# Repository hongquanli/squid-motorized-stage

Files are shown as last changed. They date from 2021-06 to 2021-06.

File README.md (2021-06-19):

# Squid motorized stages
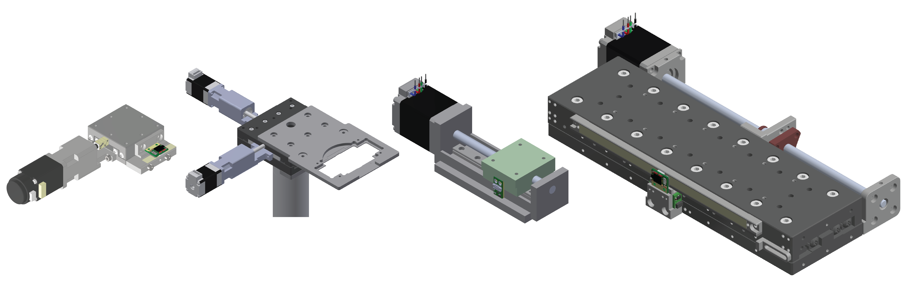
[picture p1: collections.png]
collections

## Stages
- [13 mm travel focus stage (ball bearing)](3%20mm%20travel%20fine%20adjustment%20ball%20bearing%20stage), with adapters for mounting Thorlabs SM1 lens tube
- [25 mm travel XY stage (ball bearing)](25%20mm%20travel%20XY%20ball%20bearing%20stage), with adapters for mounting glass slide or 35 mm glass bottom dish
- [50 mm travel XY stage (linear guideway with recirculating bell bearings)](50%20mm%20travel%20linear%20guideway%20stage%20for%20non-cantilevered%20load), used in gravitymachine
- [130 mm travel X or XY stage (cross roller bearing)](130%20mm%20travel%20cross%20roller%20bearing%20stage), with kinematic well plate holder. Also used for Nautilus (Octopi/Squid-based plate reader)

## Stage controller PCB


Right now we're using a custom PCB stack for controlling the stages. The microcontroller is an Arduino Due (we intend to switch to teensy 4.1) and the stepper motor drivers are Trinamic TMC2209 SilentStepSticks (we intend to switch to using Trinamic motion controller TMC4361 + one of the Trinamic stepper drivers so that the limit switches and encoders are interfaced by the motion controllers instead of the micontroller, which will also reduce the number of GPIOs needed from the micontroller). 

The driver stack development is led by Ethan (Github repo: [link](https://github.com/prakashlab/octopi-driver-board)). Currently used the PCB and PCBA fab files can be found on the squid-imaging website [www.squid-imaging.org](www.squid-imaging.org) and in [driver stack](driver%20stack).

## Control panel


BOM of the control panel can be found in [control panel](control%20panel)

## Software
The stages can be controled with the Arduino firmware and python software: 

Microscope software Github repo: [link](https://github.com/hongquanli/octopi-research), simple GUI example: [link](https://github.com/hongquanli/squid-tutorials/tree/main/example_stepper_control) (we also explained how the software is written in these two short READMEs: [overview](https://github.com/hongquanli/squid-tutorials/tree/main/example_led_control), [more detailed note](https://github.com/hongquanli/squid-tutorials/tree/main/example_led_control/software)).

## References
[1] Hongquan Li, Deepak Krishnamurthy, Ethan Li, Pranav Vyas, Nibha Akireddy, Chew Chai, Manu Prakash, "**Squid: Simplifying Quantitative Imaging Platform Development and Deployment**." BiorXiv [ [Github](https://github.com/hongquanli/octopi-research) | [preprint](https://doi.org/10.1101/2020.12.28.424613) | [website](https://squid-imaging.org)]

[2] Deepak Krishnamurthy, Hongquan Li, François Benoit du Rey, Pierre Cambournac, Adam G. Larson, Ethan Li, and Manu Prakash. "**Scale-free vertical tracking microscopy.**" Nature Methods 17, no. 10 (2020): 1040-1051. [ [Github](https://github.com/deepakkrishnamurthy/gravitymachine-research) | [paper](https://www.nature.com/articles/s41592-020-0924-7) | [website](https://gravitymachine.org) ]

[3] Janie R. Byrum, Eric Waltari, Owen Janson, Syuan-Ming Guo, Jenny Folkesson, Bryant B. Chhun, Joanna Vinden, Ivan E. Ivanov, Marcus L. Forst, Hongquan Li, Adam G. Larson, Wesley Wu1, Cristina M. Tato, Krista M. McCutcheon, Michael J. Peluso, Timothy J. Henrich, Steven G. Deeks, Manu Prakash, Bryan Greenhouse, John E. Pak, Shalin B. Mehta. "**multiSero: Open multiplex-ELISA platform for analyzing antibody responses to SARS-CoV-2 infection**." bioRxiv [ [preprint](https://doi.org/10.1101/2021.05.07.21249238) | [Github](https://github.com/czbiohub/pysero) ]

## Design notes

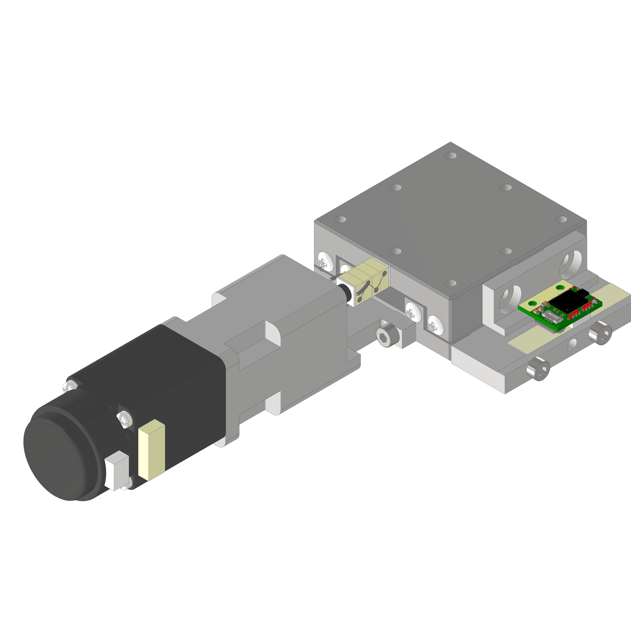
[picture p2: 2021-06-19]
13 mm travel fine adjustment ball bearing stage/CAD rendering.png

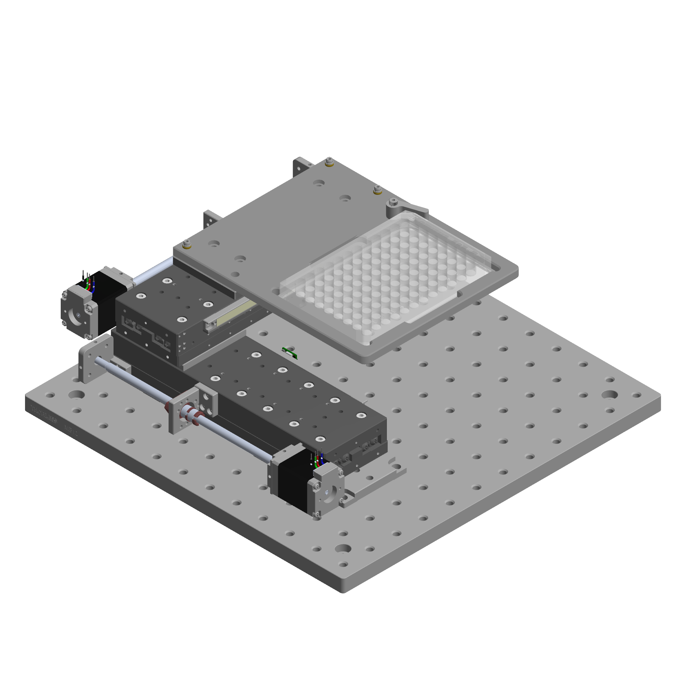
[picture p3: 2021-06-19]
130 mm travel cross roller bearing stage/motorized VRU3205 XY v2.0.png

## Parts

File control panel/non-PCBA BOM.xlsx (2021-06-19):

# | Description | Vendor | Part Number | Qty | Unit Price | Vendor Contact | Image Reference
 | Control Panel
1 | ~~analoy joystick (HE1, 2 Axis Low Profile Locked Z, 1 Button, Square Limiter, Rear Mount, 0-5v, Black)~~ | Ruffy Controls | ~~HE1-61-S-D-1-BK~~ | 1 | $135.00 | http://ruffycontrols.com/
 | analoy joystick (HE1, 2 Axis Low Profile Locked Z, 1 Button, Square Limiter, Rear Mount, 0-3.3v output, Black) | Ruffy Controls | HE1-61-S-D-3.3-BK | 1 | $135.00
2 | pre-crimped jumper for joystick | Digi-Key | H3BBG-10106-B4 | 6 | $0.77
3 | connector socket for joystick cable assembly | Digi-Key | DF11-12DS-2C | 2 | $0.25
4 | (PCBA) SMD header for joystick cable assembly | Digi-Key | DF11C-12DP-2V(57) | 1 | $2.11
5 | rotary encoder (magnetic) for focus adjustment | Digi-Key | EMS22Q31-B28-LS4 | 1 | $31.96
6 | knob for focus adjustment | Digi-Key | KLN1250B1/4 | 1 | $18.16
7 | cable assembly for rotary encoder | Digi-Key | A06KR06KR26E102B | 1 | $1.16
8 | (PCBA) SMD header for rotary encoder | Digi-Key | B6B-PH-SM4-TB(LF)(SN) | 1 | $0.77
9 | (PCBA) rotary potentiometer | Digi-Key | PCW1J-C24-BAB103L | 1 | $5.37
10 | knob for rotary potentiometer | Digi-Key | OEDA-63-4-5 | 2 | $7,74
11 | toggle switch with LED indicator | Digi-Key | M2112TFW02 | 1 | $11.96
12 | quick-connector contact for the toggle switch | Digi-Key | 61454-1 | 4 | $0.28
13 | (PCBA) SMD header for toggle switch | Digi-Key | 1778719 | 1 | $1.28
14 | plug for toggle switch | Digi-Key | 1704857 | 1 | $1.42
15 | ~~(PCBA) 12 pin picolock SMD header for driver stack connection~~ | ~~Digi-Key~~ | ~~5040501291~~ | ~~1~~ | ~~$1.76~~
16 | ~~(PCBA) 4 pin picolock SMD header for driver stack connection~~ | ~~Digi-Key~~ | ~~5040500491~~ | ~~1~~ | ~~$0.85~~
 | (PCBA) 8 pin picolock SMD header for driver stack connection | Digi-Key | 5040500891 | 1
 | (PCBA) 6 pin picolock SMD header for driver stack connection | Digi-Key | 5040500691 | 1
17 | ~~12 pin picklock cable assembly ~~ | ~~Digi-Key~~ | ~~151321206~~ | ~~1~~ | ~~$7.28~~
18 | ~~4 pin picklock cable assembly ~~ | ~~Digi-Key~~ | ~~151320406~~ | ~~1~~ | ~~$3.64~~
 | 8 pin picklock cable assembly | Digi-Key | 151320806
 | 6 pin picklock cable assembly | Digi-Key | 151320606
22 | ~~5V step-up~~ | Pololu | ~~2564~~ | 1 | $4.49
23 | aluminum enclosure | polycase | al-77p | 1 | $14.26
24 | thread-forming screws for the case | McMaster-Carr | 93878A148 | 6
Total: $363.94

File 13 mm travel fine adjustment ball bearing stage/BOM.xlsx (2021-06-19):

# | Description | Vendor | Part Number / File for CNC machining | Qty | Unit Price | Vendor Contact | Image Reference
 | Motorized Focus Assembly
1 | ball bearing linear stage, stainless steel, ±6.5mm | dg-sl (http://www.dg-sl.com/) | LBX40-C (product page) (http://www.dg-sl.com/plus/view.php?aid=367) | 1 | $61.14 | https://seln.taobao.com
2 | adapter for mounting SM1TC to LBX40-C | XTJ-tech | adapter_LBX40_SM1TC(thick)_v2.zip (https://drive.google.com/file/d/1vSxkDf_U7Hy0DEYcMtg9wJZE37Ds1pc6/view?usp=sharing) | 1 | $25.00 | katie@xtj-tech.com
3 | adapter for mounting LBX40-C to C1511 | XTJ-tech | adapter_LBX40_C1511_v3.zip (https://drive.google.com/file/d/1vVJ2LQsEshlLTpUiCyFs6SZvvZQxfeaH/view?usp=sharing) | 1 | $25.00
4 | adapter for mounting 21H4U to LBX40-C | XTJ-tech | adapter_LBX40_21H4U_v3.stp (https://drive.google.com/file/d/1vdc5DMPaTfWaKH6Y-Y7UMupx3H2Tfn9w/view?usp=sharingg) | 1 | $55.00
5 | size 8 captive linear actuator, 6e-5 in/step | Haydon kerk | 21H4U-2.5-A98 v1 (based on 21H4U-2.5-907) (https://prototypes.haydonkerk.com/ecatalog/hybrid-linear-actuators/en/linear-actuator-21H4U-2.5-907) | 1 | $130.45
6 | optional piezo stack actuator, 11.2 um travel (no load) | Thorlabs | PK2FMP2 | 0 | $62.25
 | optional amplified piezo actuator, 220 um travel (no load) | Thorlasb | PK2FSF1 | 0 | $366.83
 | optional amplified piezo actuator, 420 um travel (no load) | Thorlasb | PK2FVF1 | 0 | $480.46
7 | Clamp for SM1 Lens Tubes | Thorlabs | SM1TC | 1 | $45.72
8 | SM1 Lens Tube, 0.3" threaded depth | Thorlabs | SM1L03 | 1 | $12.52
9 | SM1 adapter for Objectives with RMS thread (Olympus, BoliOptics) | Thorlabs | SM1A3 | 1 | $18.50
10 | SM1 adapter for Nikon Objectives | Thorlabs | SM1A12 | 0 | $21.86
11 | M3 x 15 mm (or 14 mm) socket head screws for mounting the top plate for LBX40-C (line 2) [11.5 mm + 3.5 mm/5mm] | McMaster-Carr | 91292A346 or 91292A027 | 4
12 | M3 x 5 mm socket head screws for mounting the LBX40-C assembly to the adapter plate for C1511 | McMaster-Carr | 91292A110 | 4
13 | 8-32 x 1/2" socket head screws for mounting the assembly to C1511 | McMaster-Carr | 92196A194 | 4
14 | 8-32 x 1/4" socket head screws for mounting SM1TC | McMaster-Carr | 92196A190 | 1
15 | M2.5 x 8 mm socket head screws for adapter mounting linear actuator assembly to LBX40-C | McMaster-Carr | 91292A012 | 2
16 | M2 x 6 mm socket head screws for mounting the linear actuator |  |  | 4
Total: $312.19
 | Motorized Focus Assembly Optical Encoder Addon (optional)
1 | Optira Incremental, 5V Input, 5nm Resolution | Celera Motion | PIA-0005-A1-05-A | 1 | RFQ (we're asked by the vendor to not disclose the price) | https://www.celeramotion.com/request-a-quote/
2 | Optira Tape Scale, 20um w/Center Index, 30mm Long | Celera Motion | 124-40030-B-I | 1 | RFQ (we're asked by the vendor to not disclose the price) | https://www.celeramotion.com/request-a-quote/
3 | adapter for mouting the optira PI encoder to LBX40-C | XTJ-tech | adapter_LBX40_Optira PI.zip (https://drive.google.com/file/d/1vdktcWQU654wsF2iJLESckWOvEwZ94rC/view?usp=sharing) | 1 | $15.00
4 | adapter for mouting the optira tape to LBX40-C | XTJ-tech | adapter_LBX40_Optira PI tape 30mm.stp (https://drive.google.com/file/d/1vjwUcNyPCBcBCZTBB1smuDJui9zGkcLM/view?usp=sharing) | 1 | $15.00
5 | M1.6 x 2 mm socket head screw for mounting the encoder | McMaster-Carr | 92290A847 (or 92000A040) | 2
6 | M3 x 3 mm low profile socket head screw for mounting the encoder adapter to LBX40-C | McMaster-Carr | 90666A100 | 2
7 | M2.5 x 18 mm socket head screw for mounting the tape adapter to LBX40-C | McMaster-Carr | 91292A028 | 2
(Total: <$400)
 | Cage Cube Addon for Epifluorescence/Patterned Illumination/Active Drift Correction/3D Focus Tracking etc. (optional)
1 | mounting adapter for CM1-DCH | XTJ-tech | adapter_CM1-DCH_v2.zip (https://drive.google.com/file/d/1vmlo_wTWzoKCbnt8HrBpzqPNQ9Hj7mCo/view?usp=sharing) | 1 | $30.00
2 | Cage Cube for Rectangular Optics | Thorlabs | CM1-DCH | 1 | $175.31
3 | Cage Cube Connector for additional CM1-DCH | Thorlabs | CM1-CC | 0 | $48.70
4 | additional cage cubes | Thorlabs | CM1-DCH | 0 | $175.31
5 | Externally SM1-Threaded End Cap | Thorlabs | SM1CP2 | 2 | $18.83
6 | 8-32 socket head screw for mounting the CM1-DCH adapter | McMaster-Carr | 92196A190 | 4
7 | 2 mm dia. x 5 mm length Dowel pin | McMaster-Carr | 91585A189 | 2
(Total: $205.31)

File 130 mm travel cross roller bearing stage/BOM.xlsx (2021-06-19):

# | Description | Vendor | Part Number / File for CNC machining | Qty | Unit Price | Vendor Contact | Image Reference
 | 130 mm travel motorized cross roller stage - single axis, bare minimum
 | SELN VRU3-205 stage, modified | dg-sl (http://www.dg-sl.com/) | SELN-VRU3-205-02 (based on http://www.dg-sl.com/plus/view.php?aid=143) | 1 | $100.00
 | PBC linear motorized lead screw | PBCLinear | https://theconfig.com/07895591C3 | 1 | $162.40
 | VRU3 motor mount | XTJ-tech | see custom machined parts folder | 1 | $20.00
 | VRU3 nut mount | XTJ-tech | see custom machined parts folder | 1 | $15.00
 | VRU3 bearing mount | XTJ-tech | see custom machined parts folder | 1 | $20.00
 | iglide® L280, sleeve bearing for fast rotating applications | Igus | https://www.igus.com/product/7?artNr=LSM-0507-05 | 1 | $1.45
 | Total: $318.85
 | XY stage with kinematic mounted plate holder
 | SELN VRU3-205 stage, modified | dg-sl (http://www.dg-sl.com/) | see custom machined parts folder | 2 | $100.00
 | PBC linear motorized lead screw | PBCLinear | https://theconfig.com/07895591C3 | 2 | $162.40
 | VRU3 motor mount | XTJ-tech | see custom machined parts folder | 2 | $20.00
 | VRU3 nut mount | XTJ-tech | see custom machined parts folder | 2 | $15.00
 | VRU3 bearing mount | XTJ-tech | see custom machined parts folder | 2 | $20.00
 | iglide® L280, sleeve bearing for fast rotating applications | Igus | https://www.igus.com/product/7?artNr=LSM-0507-05 | 1 | $1.45
 | limit switch magnet mount | XTJ-tech | see custom machined parts folder | 4 | $10.00
 | limit switch mount | XTJ-tech | see custom machined parts folder | 2 | $20.00
 | VRU3 base | XTJ-tech | see custom machined parts folder | 2 | $25.00
 | XY adapting plate | XTJ-tech | see custom machined parts folder | 1 | $15.00
 | well plate holder (MIC-6 Al) | XTJ-tech | see custom machined parts folder | 1 | $50.00
 | well plate holder base | XTJ-tech | see custom machined parts folder | 1 | $25.00
 | well plate clamp | XTJ-tech | see custom machined parts folder | 1 | $10.00
 | custom torsion spring | XTJ-tech | see custom machined parts folder | 1 | $1.50
 | sapphire contact pad | Thorlabs | https://www.thorlabs.com/thorproduct.cfm?partnumber=P25SK2 | 1 | $7.09
 | Threaded Bushing | Thorlabs | https://www.thorlabs.com/thorproduct.cfm?partnumber=N100B2P | 3 | $4.96
 | F19SS050 Adjusters | Thorlabs | https://www.thorlabs.com/thorproduct.cfm?partnumber=F19SS050 | 3 | $4.69
 | Locking Collar | Thorlabs | https://www.thorlabs.com/thorproduct.cfm?partnumber=F19SC1 | 3 | $5.51
 | Total: $920.32
 | Optional or magnetic linear encoders and scales
 | RLC2IC magnetic increamental encoder + scale, 0.244 um resolution | RLS | https://www.rls.si/eng/rlc2ic-miniature-linear-and-rotary-pcb-level-incremental-magnetic-encoder?partNumbers=RLC2ICA13BB00A00%2CMS05BM156AM078 | 1 | $103.10
 | Optira™ Series – PI optical encoder, down to 5 nm resolution | Celera Motion | https://www.celeramotion.com/microe/products/linear-encoders/nano/optira-series-pi/ | 1 | RFQ
 | MS 15 optical encoder, down to 50 nm resolution | RSF | https://www.rsf.at/en/products/length-measurement/exposed-models/ms15/ | 1 | RFQ

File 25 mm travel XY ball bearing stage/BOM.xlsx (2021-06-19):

# | Description | Vendor | Part Number / File for CNC machining | Qty | Unit Price | Vendor Contact | Image Reference
 | 30 mm x 30 mm travel motorized stage (the specified travel of the stage is 25 mm but actual travel is larger - close to 30 mm x 30 mm)
1 | cross roller bearing linear stage, aluminum, ±12.5mm | dg-sl (http://www.dg-sl.com/) | LY80-CB (product page) (http://www.dg-sl.com/plus/view.php?aid=430) | 1 | $168.00 | https://seln.taobao.com
2 | size 8 captive linear actuator | Nanotec | LGA201S06-B-TDBA-038 | 2 | $152.00 | https://us.nanotec.com/products/2838-lga201s06-b-tdba-038
3 | adapter for mounting linear actuator to LY80-CB | XTJ-tech | adapter_LY80-CB_LGA20.stp (https://drive.google.com/file/d/1vr1I-hMQn7dr2koNRlnyY5aXdwgQq6TP/view?usp=sharing) | 2 | $25.00
4 | adapter for mounting LY80-CB to 1.5" post | XTJ-tech | adapter_LY80-CB_post_v2.zip (https://drive.google.com/file/d/1vok4e4640o_f0QpNSyhCTgKP9MVfUR3V/view?usp=sharing) | 1 | $20.00
5 | glass slide/petridish holder (MIC-6 Al) | XTJ-tech | sample holder_v2.1.stp (https://drive.google.com/file/d/1voHS16IwZe9Dwx52aForPZ1XCP-zlX9y/view?usp=sharing) | 1 | $35.00
6 | M4 x 10 mm socket head screw | McMaster-Carr | 91292A116 | 4
7 | 1/4-20 set screw |  |  | 1
8 | M4 low profile socket head screw (4 mm length) | McMaster-Carr | 92855A401 | 4
Total: $577.00

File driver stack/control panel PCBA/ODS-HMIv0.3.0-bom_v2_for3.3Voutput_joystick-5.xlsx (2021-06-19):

ODS-HMIv0.3.0-bom-2
Designator | Quantity | Supplier Link | Component Name | Manufacturer | Manufacturer Part # | Footprint | Supplier | Supplier Part # | Supplier Description | Mounting Type | Notes
J1 | 1 | https://www.digikey.com/en/products/detail/molex/5040500891/4693487 | 1x8 1.5mm Pitch Right-Angle Header | Molex | 5040500891 | 1x8POS | Digi-Key | WM14421CT-ND | CONN HEADER SMD R/A 8POS 1.5MM | SMT
J2 | 1 | https://www.digikey.com/en/products/detail/5040500691/WM10143CT-ND/4357143 | 1x6 1.5mm Pitch Right-Angle Header | Molex | 5040500691 | 1x6POS | Digi-Key | WM10143CT-ND | CONN HEADER SMD R/A 6POS 1.5MM | SMT
J3 | 1 | https://www.digikey.com/en/products/detail/jst-sales-america-inc/B6B-PH-SM4-TBT-LF-SN/9918862 | JST 1x6 Right-Angle Shrouded PH Header | JST | B6B-PH-SM4-TBT(LF)(SN) | 1x6POS | Digi-Key | 455-3363-1-ND | CONN HEADER SMD 6POS 2MM | SMT
U1,U2 | 2 | https://www.digikey.com/en/products/detail/bourns-inc/PCW1J-C24-BAB103L/3534177 | Rotary Potentiometer | Bourns | PCW1J-C24-BAB103L | 1x3POS | Digi-Key | PCW1J-C24-BAB103L-ND | POT 10K OHM 3/4W PLASTIC LINEAR | PTH
J4,J5 | 2 | https://www.digikey.com/en/products/detail/phoenix-contact/1778719/5131543 | Phoenix 1x4 Shrouded SSL Header | Phoenix Contact | 1778719 | 1x4POS | Digi-Key | 277-10160-1-ND | HEADER 4POS SMT WHITE | SMT
CN1 | 1 | https://www.digikey.com/en/products/detail/hirose-electric-co-ltd/DF11C-12DP-2V-57/4282018 | Hirose 2x6 Shrouded DF11 Header | Hirose | DF11C-12DP-2V(57) | 2x6POS | Digi-Key | H124541CT-ND | CONN HEADER SMD 12POS 2MM | SMT
R1 | 1 | https://www.digikey.com/en/products/detail/yageo/RC0805FR-0749R9L/727984 | 49.9 0805 resistor | Yageo | RC0805FR-0749R9L | 805 | Digi-Key | 311-49.9CRTR-ND | RES SMD 49.9 OHM 1% 1/8W 0805 | SMT
R3,R5 | 3 | https://www.digikey.com/en/products/detail/yageo/RC0805FR-0710KL/727535 | 0ohm 0805 resistor | Yageo | RC0805FR-0710KL | 805 | Digi-Key | 311-10.0KCRTR-ND | RES SMD 10K OHM 1% 1/8W 0805 | SMT
R2 | 3 | https://www.digikey.com/en/products/detail/yageo/RC0805FR-0710KL/727535 | 10K 0805 resistor | Yageo | RC0805FR-0710KL | 805 | Digi-Key | 311-10.0KCRTR-ND | RES SMD 10K OHM 1% 1/8W 0805 | SMT
R4,R6 | 2 | https://www.digikey.com/en/products/detail/yageo/RC0805FR-0720KL/727720 | DNI | Yageo | RC0805FR-0720KL | 805 | Digi-Key | 311-20.00KCRCT-ND | RES SMD 20K OHM 1% 1/8W 0805 | SMT
R7 | 1 | https://www.digikey.com/en/products/detail/yageo/RC0805FR-07499RL/727986 | 499 0805 resistor | Yageo | RC0805FR-07499RL | 805 | Digi-Key | 311-499CRTR-ND | RES SMD 499 OHM 1% 1/8W 0805 | SMT

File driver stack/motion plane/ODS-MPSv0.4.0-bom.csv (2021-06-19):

Designator | Quantity | Supplier Link | BOM ID | Component ID | Image | Component Name | Manufacturer | Manufacturer Part # | Footprint | Supplier | Supplier Part # | Supplier Description | Mounting Type | Notes
H1,H3,H2 | 3 | https://www.pololu.com/product/2749 | 2 | 5 |  | 2x20 Female Header, Tall Stacking | Sullins Connector Solutions | PPPC202LFHN-M53 RC | 2x20POS | Pololu | 2749 | Stackable 0.100″ Female Header with Extra 0.3″ Spacer: 2x20-Pin, Straight | PTH | The female side should be on the underside of the board, while the male pins should stick up.
H4, H5, H6, H7, H8, H9, H10, H11 | 8 | https://www.digikey.com/product-detail/en/sullins-connector-solutions/NPPC081KFXC-RC/S5639-ND/776098 | 4 | 17 |  | 1x8 Female SMT Header | Sullins Connector Solutions | NPPC081KFXC-RC | 1x8POS | Digi-Key | S5639-ND | CONN HDR 8POS 0.1 GOLD SMD | SMT
C1,C2,C3,C4 | 4 | https://www.digikey.com/product-detail/en/nichicon/UCD1E470MCL1GS/493-6385-1-ND/3438899 | 6 | 18 |  | 47uF Electrolytic Capacitor | Nichicon | UCD1E470MCL1GS | 6.6mmx6.6mm | Digi-Key | 493-6385-1-ND | CAP ALUM 47UF 20% 25V SMD | SMT
J5 | 1 | https://www.digikey.com/product-detail/en/cui-devices/PJ-037AH-SMT-TR/CP-037AHPJCT-ND/1530998 | 7 | 19 |  | DC Power Jack | CUI Devices | PJ-037AH-SMT-TR | SMT | Digi-Key | CP-037AHPJCT-ND | CONN PWR JACK 2X5.5MM SOLDER | SMT
LED1,LED2 | 2 | https://www.digikey.com/product-detail/en/everlight-electronics-co-ltd/17-21SYGC-S530-E2-TR8/1080-1500-1-ND/7707772 | 8 | 20 |  | Green Indicator LED | Everlight Electronics | 17-21SYGC/S530-E2/TR8 | 805 | Digi-Key | 1080-1500-1-ND | LED YELLOW/GREEN CLEAR 0805 SMD | SMT
R1,R3 | 2 | https://www.digikey.com/product-detail/en/%E5%9E%88-%C3%A1/RC1206FR-071KL/311-1-00KFRCT-ND/731334 | 9 | 21 |  | 1K 1206 Resistor | Yageo | RC1206FR-071KL | 1206 | Digi-Key | 311-1.00KFRCT-ND | RES SMD 1K OHM 1% 1/4W 1206 | SMT
R2 | 1 | https://www.digikey.com/product-detail/en/%E5%9E%88-%C3%A1/RC1206FR-07100RL/311-100FRCT-ND/731438 | 10 | 22 |  | 100 1206 Resistor | Yageo | RC1206FR-07100RL | 1206 | Digi-Key | 311-100FRCT-ND | RES SMD 100 OHM 1% 1/4W 1206 | SMT
J1,J2,J3,J4 | 4 | https://www.digikey.com/product-detail/en/phoenix-contact/1814935/277-9965-1-ND/4696094 | 11 | 30 |  | 1x4 Feed-Through Header | Phoenix Contact | 1814935 | 1x4POS | Digi-Key | 277-9965-1-ND | CONN HEADER 4POS 2.5MM SMD | SMT
J7,J8,J9,J10 | 4 | https://www.digikey.com/product-detail/en/jst-sales-america-inc/S6B-ZR-SM4A-TF-LF-SN/455-1610-1-ND/858041 | 12 | 25 |  | 1x6 1.5mm Pitch Right-Angle Header | JST | S6B-ZR-SM4A-TF(LF)(SN) | 1x6POS | Digi-Key | 455-1610-1-ND | CONN HEADER SMD R/A 6POS 1.5MM | SMT
J11 | 1 | https://www.digikey.com/product-detail/en/molex/0022292041/WM2746-ND/1130590 | 13 | 26 |  | 1x4 KK 254 Male Header | Molex | 22292041 | 1x4POS | Digi-Key | WM2746-ND | CONN HEADER VERT 4POS 2.54MM | PTH | Solder so that the plastic tab is closer to the outer perimeter of the board.
U2,U3 | 2 | https://www.digikey.com/product-detail/en/nexperia-usa-inc/74LVC07AD-118/1727-3089-1-ND/946746 | 14 | 27 |  | 6-Bit Buffer | Nexperia | 74LVC07AD,118 | 14-SOIC | Digi-Key | 1727-3089-1-ND | IC BUFFER NON-INVERT 5.5V 14SO | SMT
J12 | 1 | https://www.digikey.com/en/products/detail/molex/5040500891/4693487 | 15 | 44 |  | 1x8 1.5mm Pitch Right-Angle Header | Molex | 5040500891 | 1x8POS | Digi-Key | WM14421CT-ND | CONN HEADER SMD R/A 8POS 1.5MM | SMT | On the underside of the board.
J13 | 1 | https://www.digikey.com/en/products/detail/5040500691/WM10143CT-ND/4357143 | 16 | 45 |  | 1x6 1.5mm Pitch Right-Angle Header | Molex | 5040500691 | 1x6POS | Digi-Key | WM10143CT-ND | CONN HEADER SMD R/A 6POS 1.5MM | SMT | On the underside of the board.
R4,R5,R6,R7,R8,R9,R10,R11,R12,R13,R14,R15 | 12 | https://www.digikey.com/en/products/detail/yageo/RC0805FR-074K7L/727929 | 17 | 33 |  | 4.7K 0805 Resistor | Yageo | RC0805FR-074K7L | 805 | Digi-Key | 311-4.70KCRCT-ND | RES SMD 4.7K OHM 1% 1/8W 0805 | SMT | On the underside of the board.

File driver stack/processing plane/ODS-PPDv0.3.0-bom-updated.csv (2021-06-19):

Designator | Comment | Quantity | Supplier Link | Component Name | Manufacturer | Manufacturer Part # | In OPL? | Footprint | Supplier | Supplier Part # | Supplier Description | Mounting Type | Notes
H1,H3,H2 |  | 3 | https://www.pololu.com/product/2749 | 2x20 Female Header, Tall Stacking | Sullins Connector Solutions | PPPC202LFHN-M53 RC | Yes | 2x20POS | Pololu | 2749 | Stackable 0.100″ Female Header with Extra 0.3″ Spacer: 2x20-Pin, Straight | PTH | Alternative: PRT-16763 (SparkFun or DigiKey)
SPI |  | 1 | https://www.pololu.com/product/1023 | 2x3 Female PTH Header | Pololu | 1023 | Yes | 2x3POS | Pololu | 1023 | 0.100" (2.54 mm) Female Header: 2x3-Pin, Straight | PTH
DUE1 | Note for ordering: do not order separately, break 1x40 header (see last line) | 1 | https://www.pololu.com/product/965 | 1X10 Male PTH Header | Pololu | 965 | Yes | 1x10POS | Pololu | 965 | 0.100" (2.54 mm) Breakaway Male Header: 1×40-Pin, Straight, Black | PTH
DUE2, DUE3, DUE5, DUE6, DUE7 | Note for ordering: do not order separately, break 1x40 header (see last line) | 5 | https://www.pololu.com/product/965 | 1X8 Male PTH Header | Pololu | 965 | Yes | 1x8POS | Pololu | 965 | 0.100" (2.54 mm) Breakaway Male Header: 1×40-Pin, Straight, Black | PTH
DUE4 | Note for ordering: do not order separately, break 1x40 header (see last line) | 1 | https://www.pololu.com/product/966 | 2x18 Male PTH Header | Pololu | 966 | Yes | 2x18POS | Pololu | 966 | 0.100" (2.54 mm) Breakaway Male Header: 2×40-Pin, Straight | PTH
J1 |  | 1 | https://www.digikey.com/en/products/detail/molex/5040500891/4693487 | 1x8 1.5mm Pitch Right-Angle Header | Molex | 5040500891 | Yes | 1x12POS | Digi-Key | WM14421CT-ND | CONN HEADER SMD R/A 8POS 1.5MM | SMT
J2,J6 |  | 2 | https://www.digikey.com/en/products/detail/5040500691/WM10143CT-ND/4357143 | 1x6 1.5mm Pitch Right-Angle Header | Molex | 5040500691 | Yes | 1x4POS | Digi-Key | WM10143CT-ND | CONN HEADER SMD R/A 6POS 1.5MM | SMT
J7,J8,J9,J10 |  | 4 | https://www.digikey.com/en/products/detail/phoenix-contact/1814663/4452958 | 1x5 Spring Clamp Terminal Block | Phoenix Contact | 1814663 | Yes | 1x5POS | Digi-Key | 277-10065-1-ND | TERM BLOCK 5POS | SMT
U1,U2 |  | 2 | https://www.digikey.com/en/products/detail/texas-instruments/SN74LV1T34DBVR/4555575 | SOT-23 Non-Inverting Buffer | Texas Instruments | SN74LV1T34DBVR | Yes | SOT-23-5 | Digi-Key | 296-37176-1-ND | IC BUF NON-INVERT 5.5V SOT23-5 | SMT
R1,R2 |  | 2 | https://www.digikey.com/en/products/detail/yageo/RC0603JR-0768RL/726821 | 68 Ohm 0603 Resistor | Yageo | RC0603JR-0768RL | Yes | 603 | Digi-Key | 311-68GRCT-ND | RES SMD 68 OHM 5% 1/10W 0603 | SMT
2.54 mm header | Part for DUE1-DUE7 | 3 | https://www.pololu.com/product/965

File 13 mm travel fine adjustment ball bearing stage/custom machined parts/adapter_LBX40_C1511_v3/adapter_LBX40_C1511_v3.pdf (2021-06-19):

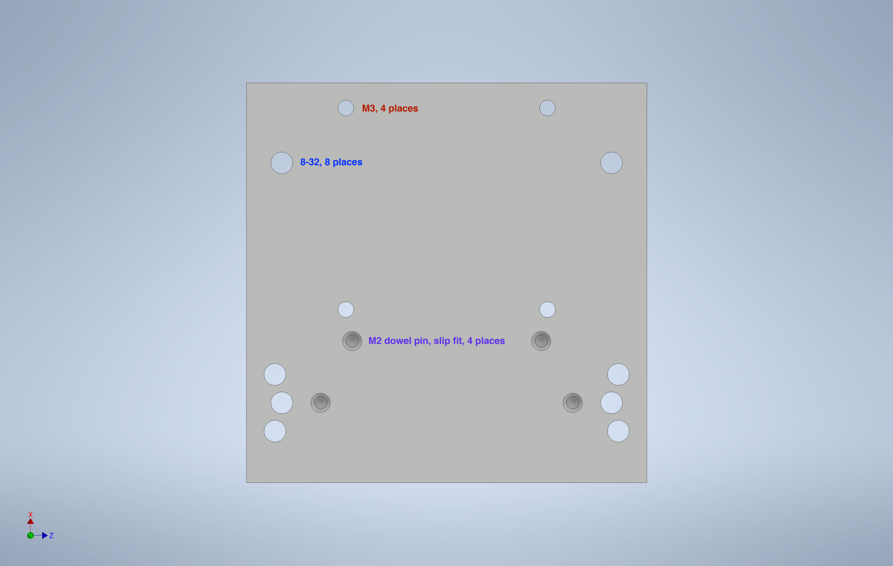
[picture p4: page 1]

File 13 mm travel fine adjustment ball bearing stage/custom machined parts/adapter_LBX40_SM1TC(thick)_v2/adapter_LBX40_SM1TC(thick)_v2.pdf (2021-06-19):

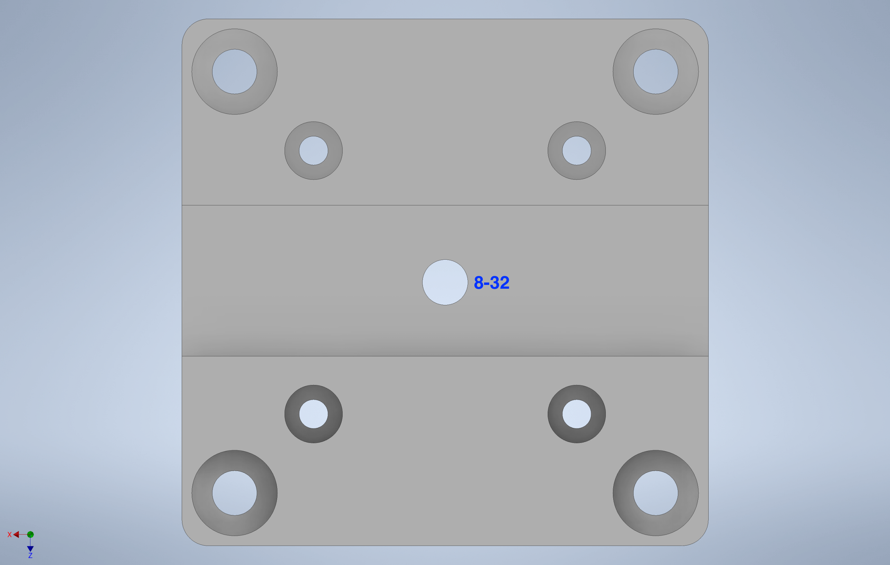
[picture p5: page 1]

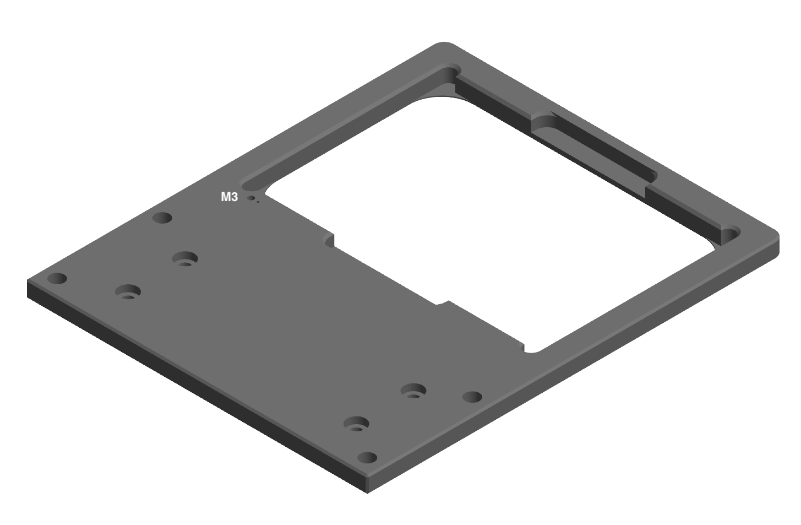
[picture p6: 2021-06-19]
130 mm travel cross roller bearing stage/custom machined parts/clamping well plate holder_20210318.png

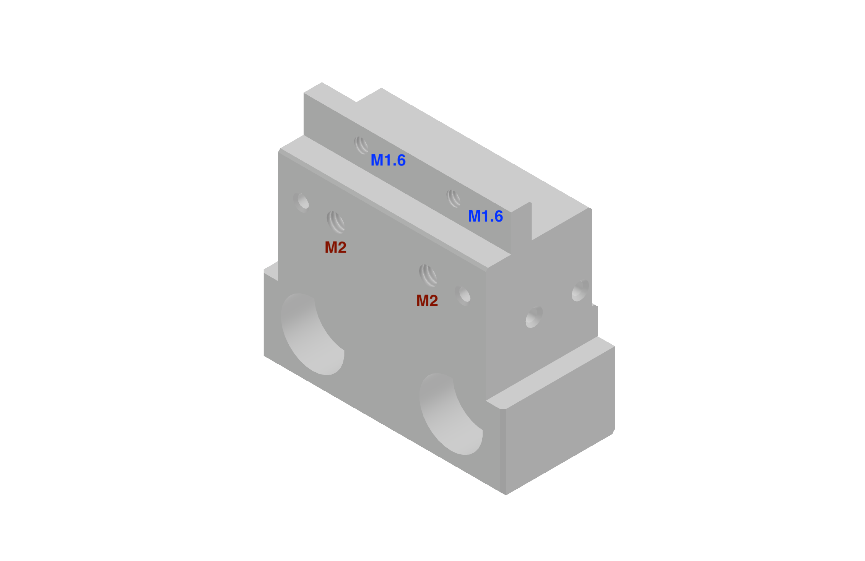
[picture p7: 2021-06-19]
130 mm travel cross roller bearing stage/custom machined parts/optira encoder mounting adapter - VRU3_20210324.png

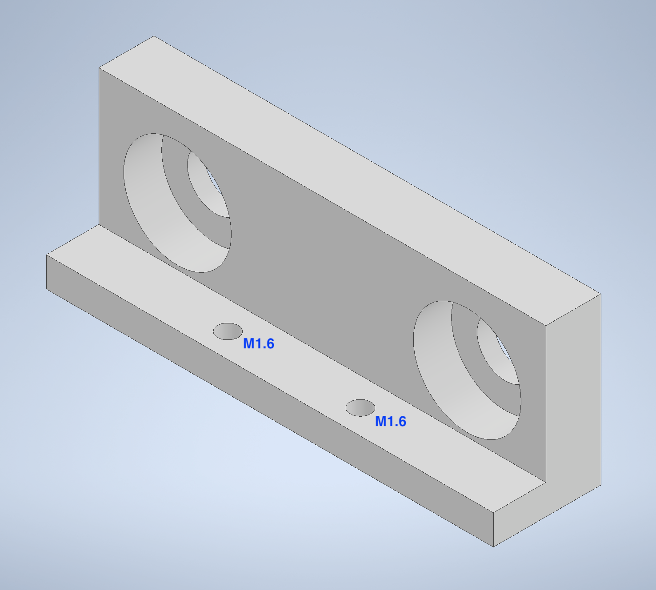
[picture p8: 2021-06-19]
13 mm travel fine adjustment ball bearing stage/custom machined parts/adapter_LBX40_Optira PI/adapter_LBX40_Optira PI.png

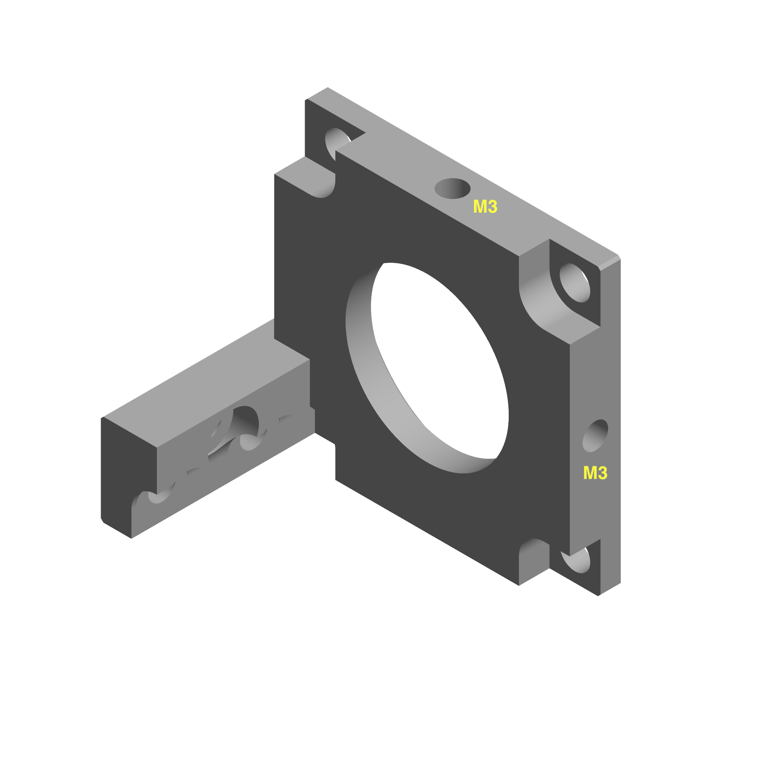
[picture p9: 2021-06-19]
130 mm travel cross roller bearing stage/custom machined parts/VRU-NEMA11 motor mount - direct attachment v2_20210325.png

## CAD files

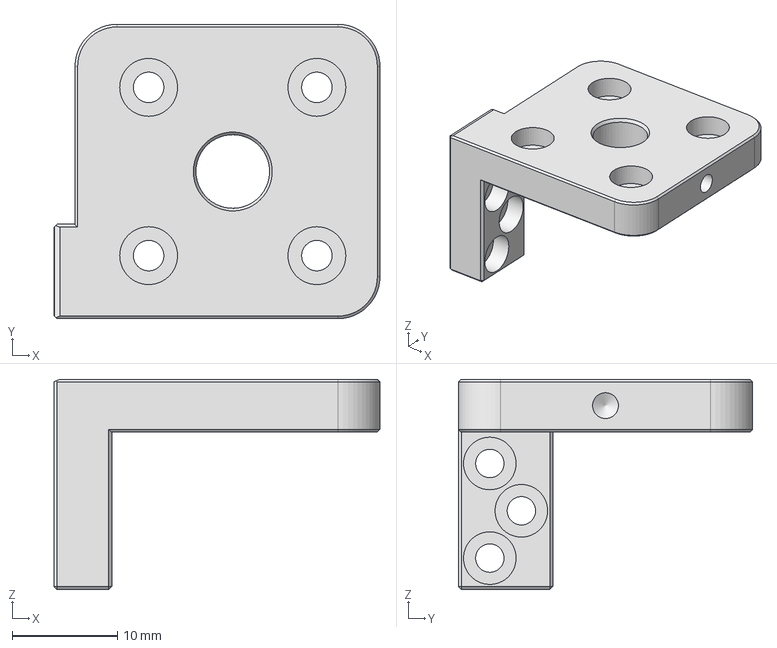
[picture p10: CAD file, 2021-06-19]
130 mm travel cross roller bearing stage/custom machined parts/VRU-NEMA11 motor mount bearing support - fullsize_20210325.stp
31.0 x 28.0 x 20.0 mm

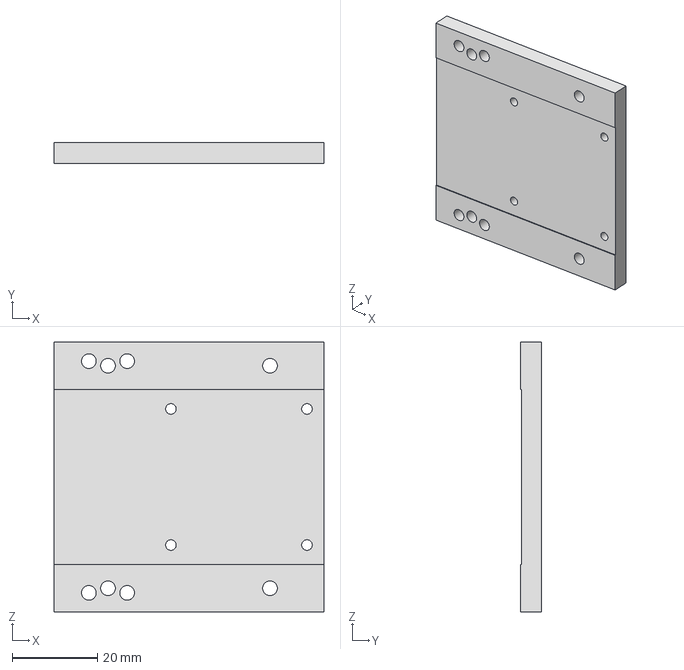
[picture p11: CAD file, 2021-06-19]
13 mm travel fine adjustment ball bearing stage/custom machined parts/adapter_LBX40_C1511_v3/adapter_LBX40_C1511_v3.stp
63.5 x 5.00 x 63.5 mm

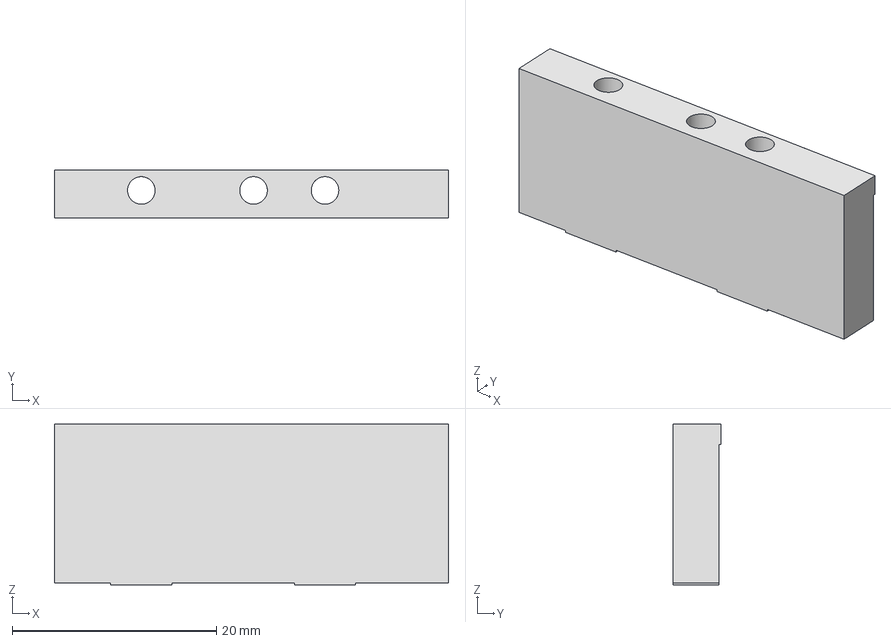
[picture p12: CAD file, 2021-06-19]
13 mm travel fine adjustment ball bearing stage/custom machined parts/adapter_LBX40_Optira PI tape 30mm.stp
38.6 x 4.70 x 15.7 mm

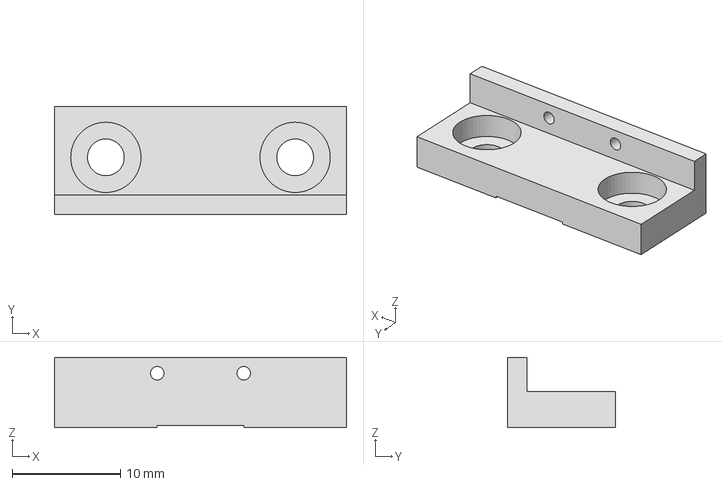
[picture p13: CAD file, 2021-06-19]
13 mm travel fine adjustment ball bearing stage/custom machined parts/adapter_LBX40_Optira PI/adapter_LBX40_Optira PI.stp
27.0 x 10.0 x 6.50 mm

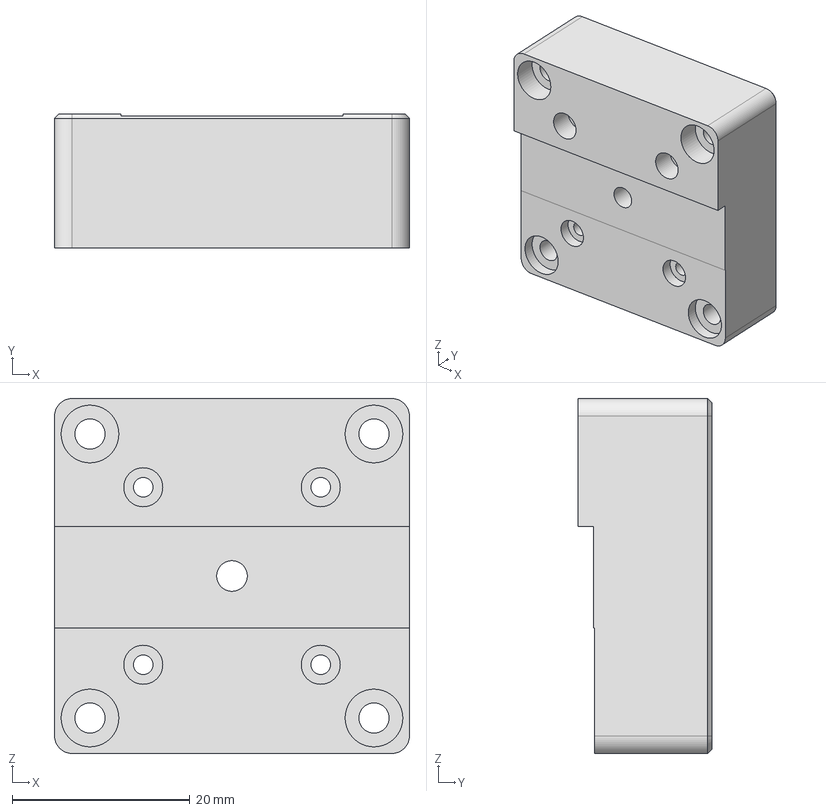
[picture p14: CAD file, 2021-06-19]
13 mm travel fine adjustment ball bearing stage/custom machined parts/adapter_LBX40_SM1TC(thick)_v2/adapter_LBX40_SM1TC(thick)_v2.stp
40.0 x 15.1 x 40.0 mm

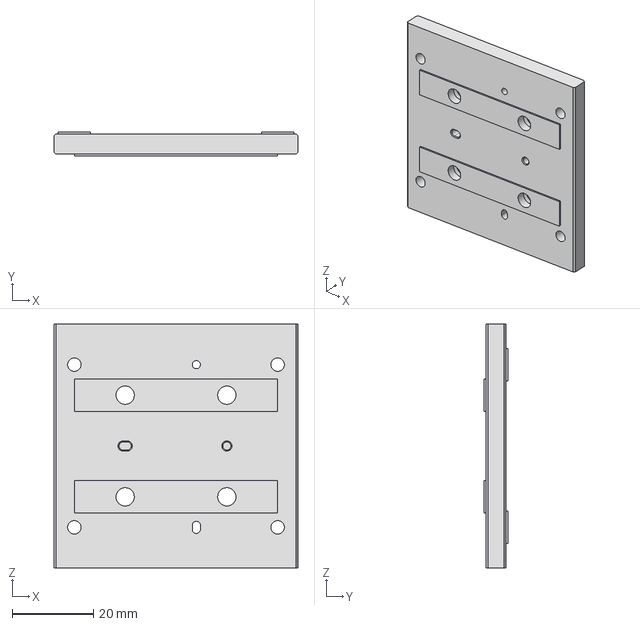
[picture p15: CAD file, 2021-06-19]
130 mm travel cross roller bearing stage/custom machined parts/VRU3 XY adapter_20210106.stp
60.0 x 6.00 x 60.0 mm

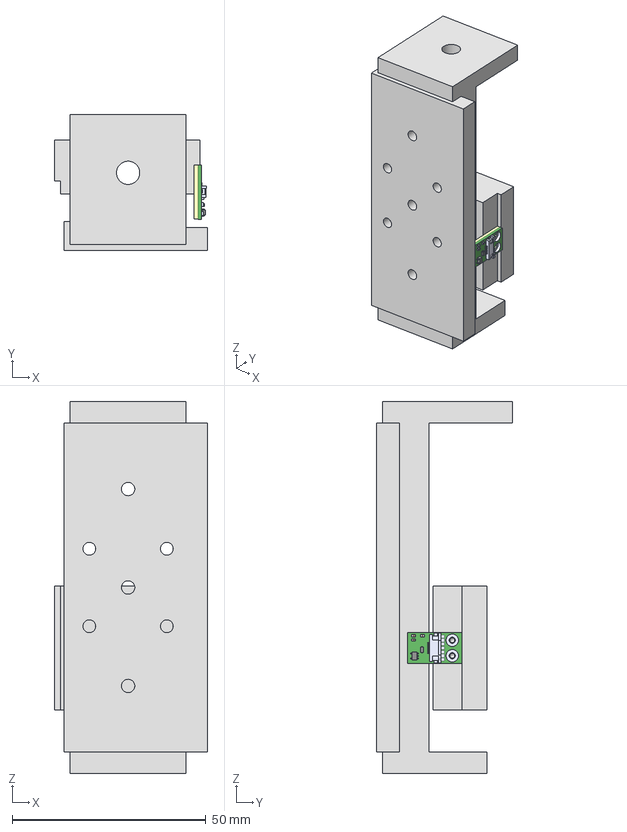
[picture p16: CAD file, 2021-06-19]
50 mm travel linear guideway stage for non-cantilevered load/custom machined parts/modified base+slider+linear encoder.stp
39.5 x 35.0 x 96.0 mm
base
slider
RLB2_8-3d

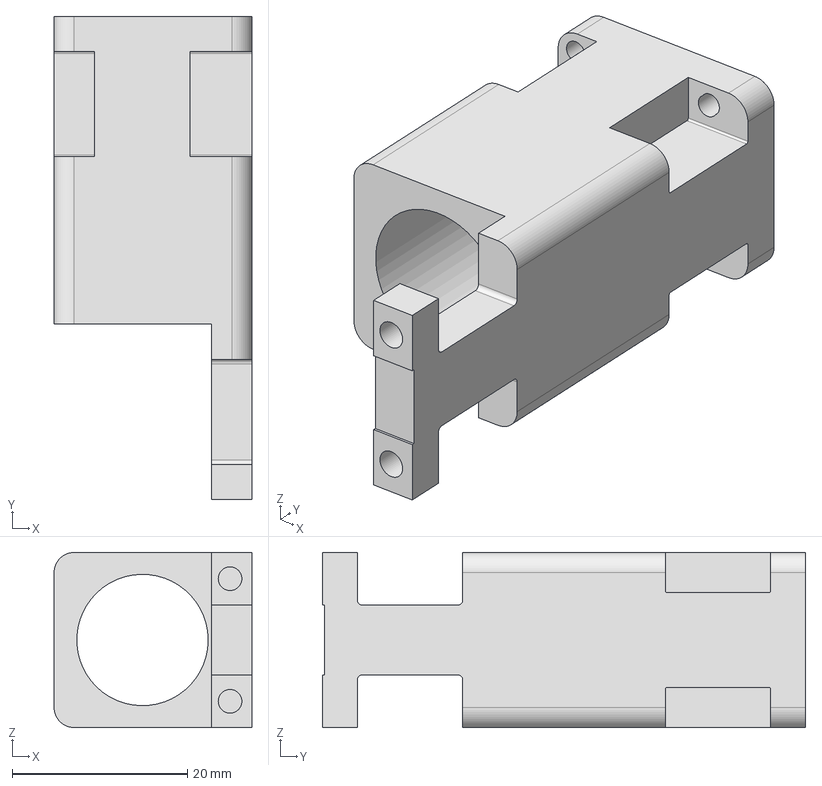
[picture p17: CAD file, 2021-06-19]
13 mm travel fine adjustment ball bearing stage/custom machined parts/adapter_LBX40_21H4U_v3.stp
22.6 x 55.2 x 20.0 mm

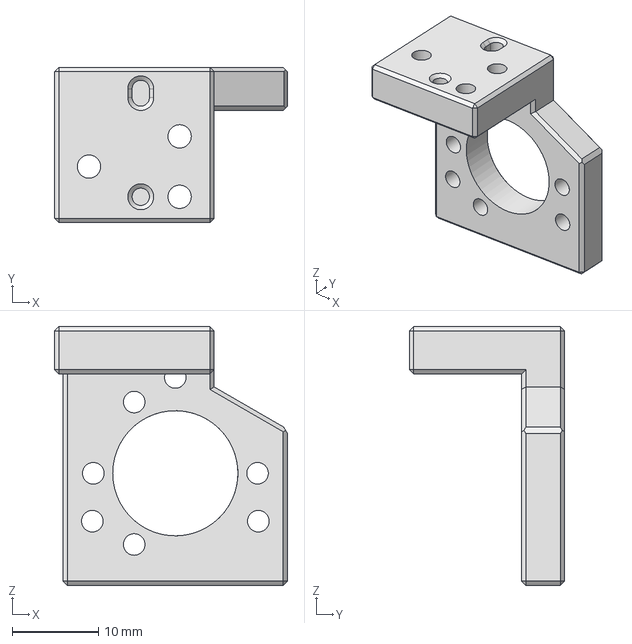
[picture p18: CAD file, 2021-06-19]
130 mm travel cross roller bearing stage/custom machined parts/VRU3 slider attachment v2_20210325.stp
27.0 x 18.0 x 30.0 mm

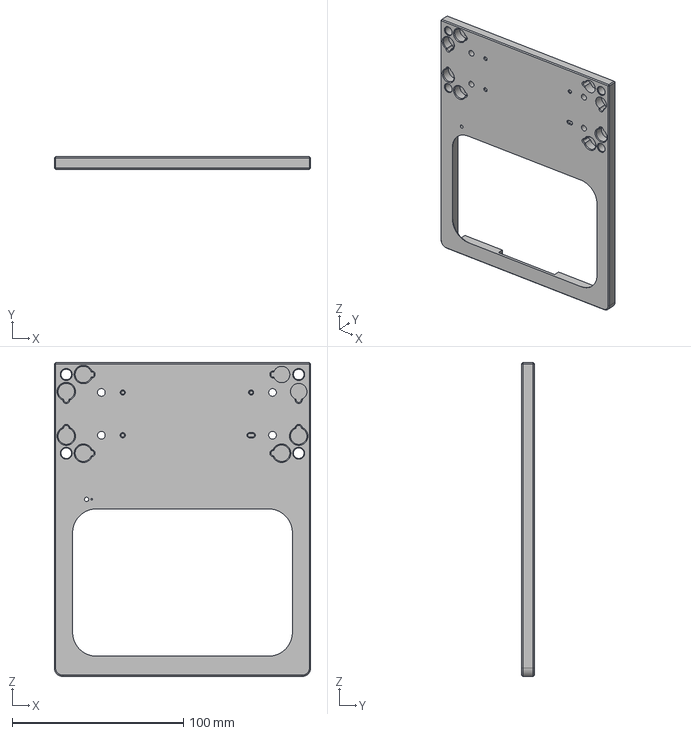
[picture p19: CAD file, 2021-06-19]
130 mm travel cross roller bearing stage/custom machined parts/clamping well plate holder_20210318.stp
149.8 x 7.50 x 183.5 mm

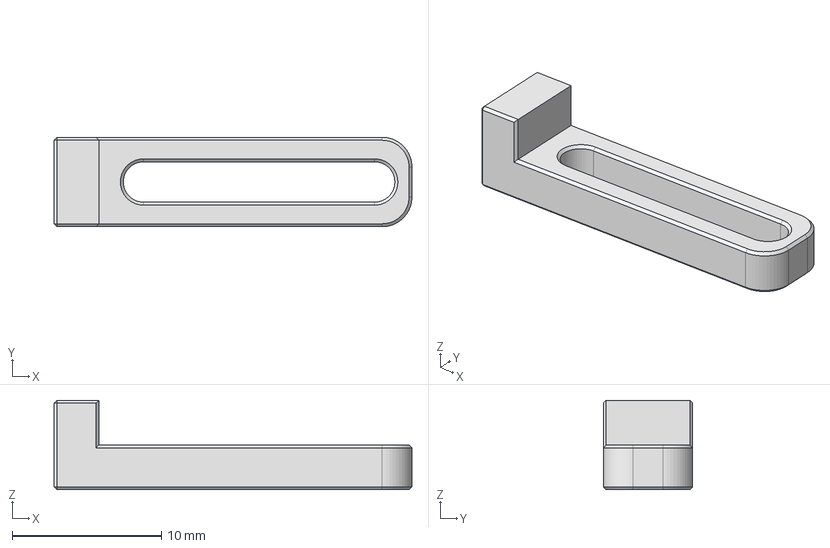
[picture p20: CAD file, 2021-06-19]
130 mm travel cross roller bearing stage/custom machined parts/VRU3 magnet mount_20210324.stp
24.0 x 6.00 x 6.00 mm

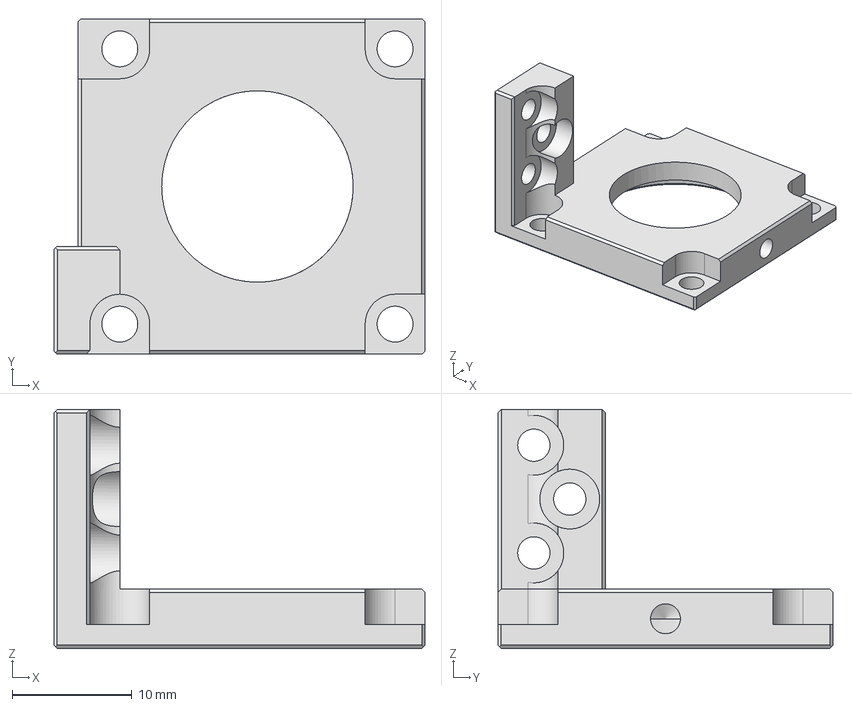
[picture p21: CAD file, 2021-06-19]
130 mm travel cross roller bearing stage/custom machined parts/VRU-NEMA11 motor mount - direct attachment v2_20210325.stp
31.0 x 28.0 x 20.0 mm

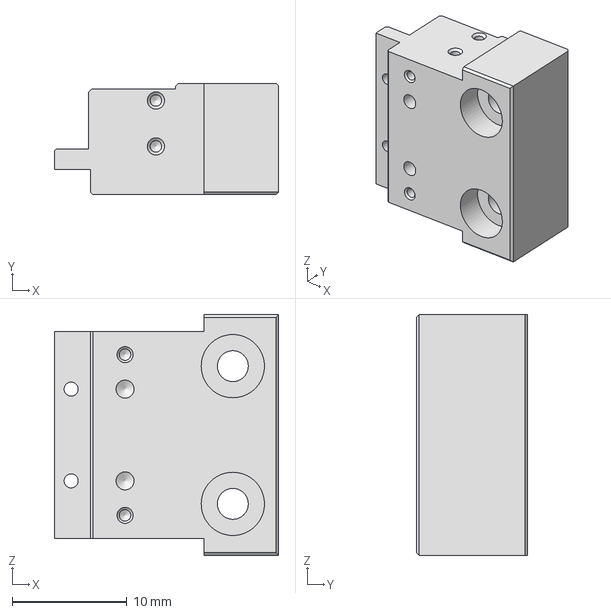
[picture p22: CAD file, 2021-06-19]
130 mm travel cross roller bearing stage/custom machined parts/optira encoder mounting adapter - VRU3_20210324.stp
19.6 x 9.71 x 21.0 mm

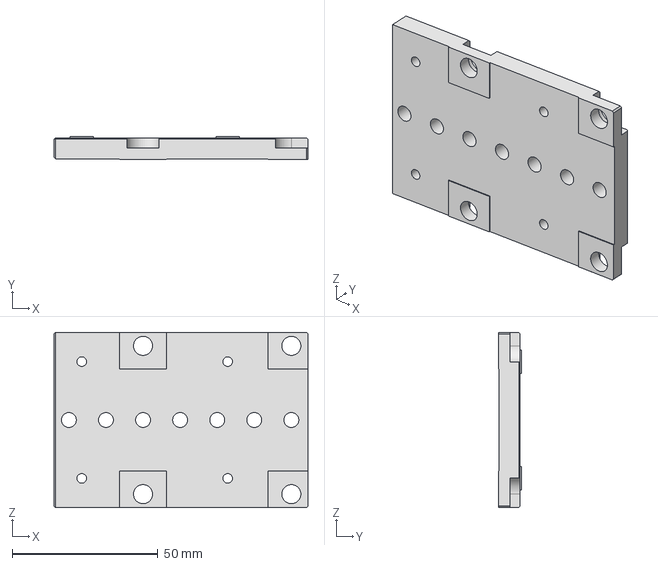
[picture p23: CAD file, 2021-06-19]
130 mm travel cross roller bearing stage/custom machined parts/VRU3 base v2_20210325.stp
87.0 x 8.00 x 60.0 mm

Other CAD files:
130 mm travel cross roller bearing stage/custom machined parts/VRU3 tape mount v2_20210325.stp

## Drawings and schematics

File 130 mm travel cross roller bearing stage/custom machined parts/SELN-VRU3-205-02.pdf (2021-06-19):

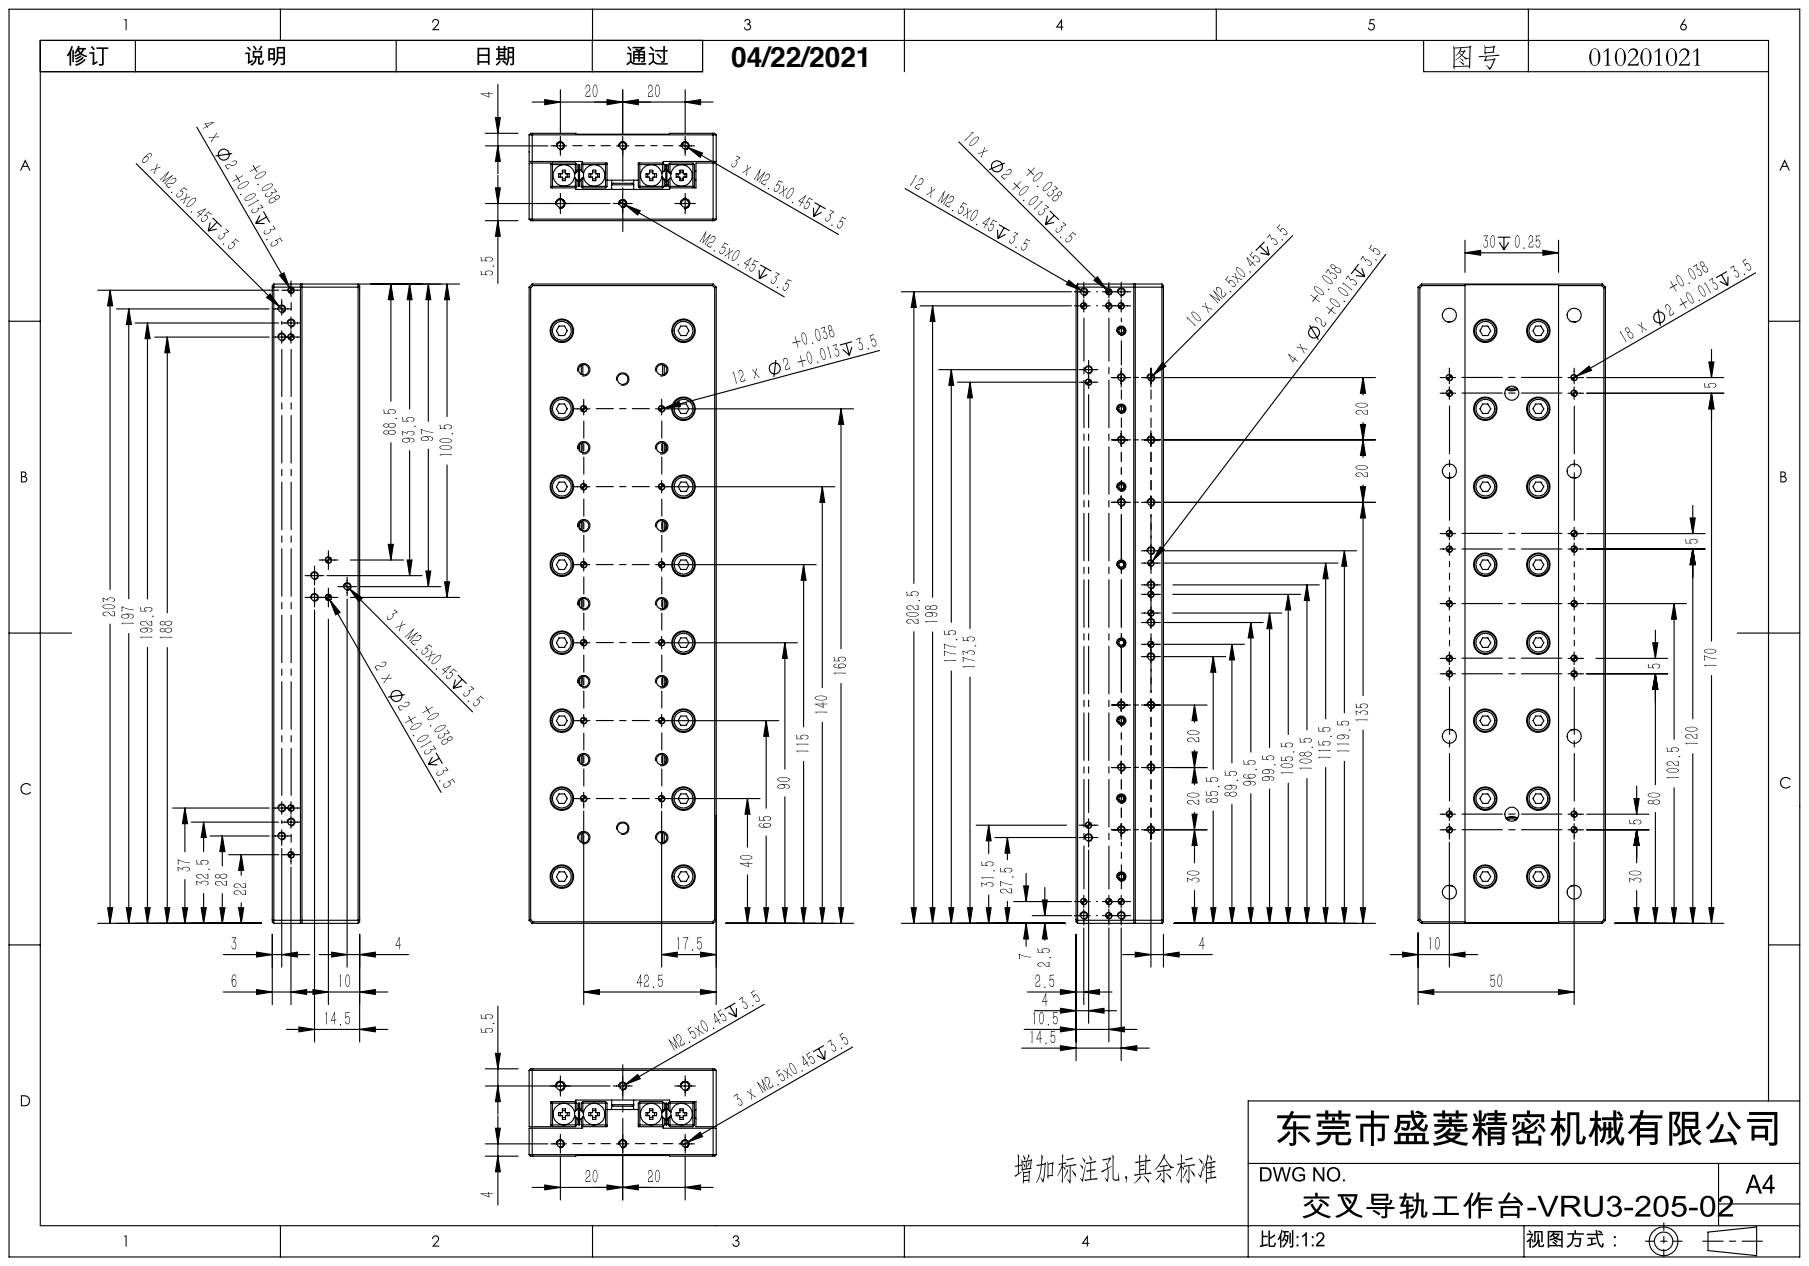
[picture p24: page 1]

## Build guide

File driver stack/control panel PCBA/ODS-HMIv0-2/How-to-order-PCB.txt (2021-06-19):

How to Order PCB

Please refer to:
https://docs.easyeda.com/en/PCB/Order-PCB
